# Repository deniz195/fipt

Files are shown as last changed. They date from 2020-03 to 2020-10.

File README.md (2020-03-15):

# FIPT: Fast impedance tortuosity 

FIPT is a measurement technique that allows a fast determination of the ionic resistance for battery electrodes. The technique is based on the work by J. Landesfeind ([DOI: 10.1149/issn.1945-7111](https://dx.doi.org/10.1149/2.1141607jes)) and then optimized for execution speed and reliability at [Battrion](https://battrion.com).

This repository contains the information to build an FIPT setup, prepare the electrolyte and the standard operating procedure (SOP) to successfully execute a measurement.

## Why?
The ionic resistance (or the MacMullin number) is a key performance metric for any battery electrode. It describes how easily ions can move through the electrode during fast charging or heavy use of the battery. It is therefore important for all manufacturers to optimize the ionic resistance of their electrodes.

Battrions Aligned Graphite Technology is a powerful way to reduce the ionic resistance by up to 50% through aligning graphite particles in an electrode.

## What do I need?

These are the things that you need to build your setup
- A 3D printer
- Couple of screws
- Kapton tape and 3mm foam.

Use the files in the `cad` folder and follow the assembly instructions.

Once you have the setup assembled, prepare the electrolyte. This needs:
- A salt (e.g. NaClO4)
- A solvent (e.g. EC:DMC)

The recipe for a useful electrolyte mixture is given in the `electrolyte` folder.

Finally, get your electrode, print out the SOP from the `sop` folder and get your first measurement. For this you need:
- An impendance analyzer
- Separator material
- A 200ul or 1ml pipette

In about 2-10min your measurement should be done.

## I got the data. What now?

Data analysis code is available at  [https://github.com/deniz195/fipt-analysis](https://github.com/deniz195/fipt-analysis)

## Contributing
Pull requests are welcome. For major changes, please open an issue first to discuss what you would like to change.

Please make sure to update tests as appropriate.

For questions please feel free to reach out to Deniz Bozyigit ([dbozyigit@battrion.com](mailto:dbozyigit@battrion.com))

## License
[GPL v3.0](https://choosealicense.com/licenses/gpl-3.0/)

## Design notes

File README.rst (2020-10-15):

===================================
FIPT: Fast impedance tortuosity
===================================



A fast way to get ionic resistance
==================================

.. intro-begin

FIPT is a measurement technique that allows a fast determination of the ionic resistance for battery electrodes. The technique is based on the work by J. Landesfeind (`DOI: 10.1149/issn.1945-7111 <https://dx.doi.org/10.1149/2.1141607jes>`_) and then optimized for execution speed and reliability at `Battrion <https://battrion.com>`_.

This repository contains the information to build an FIPT setup, prepare the electrolyte and the standard operating procedure (SOP) to successfully execute a measurement.

For a quick introduction `check out our video. <https://youtu.be/r1cBf72wSwA>`_ 

.. intro-end

Why?
====

.. why-begin

The ionic resistance (or the MacMullin number) is a key performance metric for any battery electrode. It describes how easily ions can move through the electrode during fast charging or heavy use of the battery. It is therefore important for all manufacturers to optimize the ionic resistance of their electrodes.

Battrions Aligned Graphite Technology is a powerful way to reduce the ionic resistance by up to 50% through aligning graphite particles in an electrode.

.. why-end

I'm sold. What do I need?
=========================

Here are the three main steps:

-	`Build your FIPT cell <https://fipt.readthedocs.io/en/latest/assembly.html>`_
-	`Get the materials <https://fipt.readthedocs.io/en/latest/materials.html>`_
-	`Measure ionic resistance (aka SOP) <https://fipt.readthedocs.io/en/latest/sop.html>`_

You find more details in the `full documentation <https://fipt.readthedocs.io/>`_

I got the data. What now?
=========================

Data analysis code is available at `fipt-analysis <https://github.com/deniz195/fipt-analysis>`_

Contribute
==========

.. contrib-begin
You can find all source files here: `<https://github.com/deniz195/fipt>`_

Pull requests are welcome. 

.. For major changes, please open an issue first to discuss what you would like to change.
.. Please make sure to update tests as appropriate.

For questions please feel free to reach out to Deniz Bozyigit (`dbozyigit@battrion.com <mailto:dbozyigit@battrion.com>`_)
.. contrib-end

License
=======
`GPL v3.0 <https://choosealicense.com/licenses/gpl-3.0/>`_

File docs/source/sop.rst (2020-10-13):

Measure ionic resistance (aka SOP)
==================================

.. include:: <isonum.txt>
.. See https://docutils.sourceforge.io/docs/ref/rst/definitions.html

.. note:: This standard operating procedure (SOP) also exists in `video form <https://www.battrion.com/fipt>`_

Prepare the workstation
-----------------------
.. warning:: When handling electrolyte always wear goggles and work in a well ventilated space.

Checklist : Gloves, googles, ethanol, wipe, FIPT cell, brush, tweezer, cutting tool, pipette, pipette tips and your electrode.

- Clean the workstation with ethanol.
- Clean the pipette, the tweezer with dry wipe.
- Set the pipette to 300ul and place the pipette tip.
- Clean all parts of the FIPT cell with the brush to remove any contamination of past measurement .
- Clean the cutting tool with the brush. Mind the blades!
- Check age of electrolyte.
- Check FIPT cell is complete: support, base, top and clamp.
- Check screw clutch setting is 0.4Nm

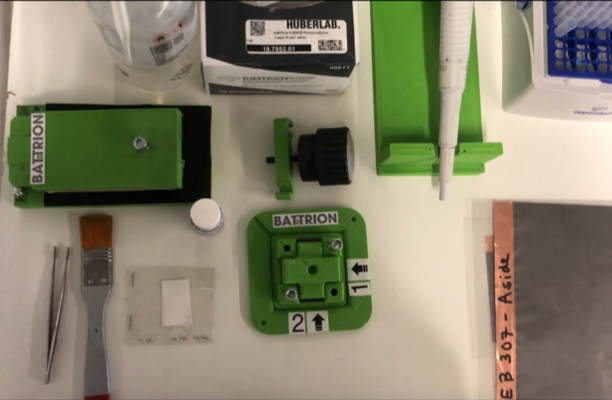
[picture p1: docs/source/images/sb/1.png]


Prepare separators
-------------------
If you have no separator pieces left, cut them in the following way:

- Cut the circular separator material (up to 3 at a time) with the triangle ruler and yellow cutting tool into **21mm wide** stripes.
- Cut the stripes into smaller pieces (21mm |times| 35mm).
- Throw out stripes with exessive wrinkling or contamination.

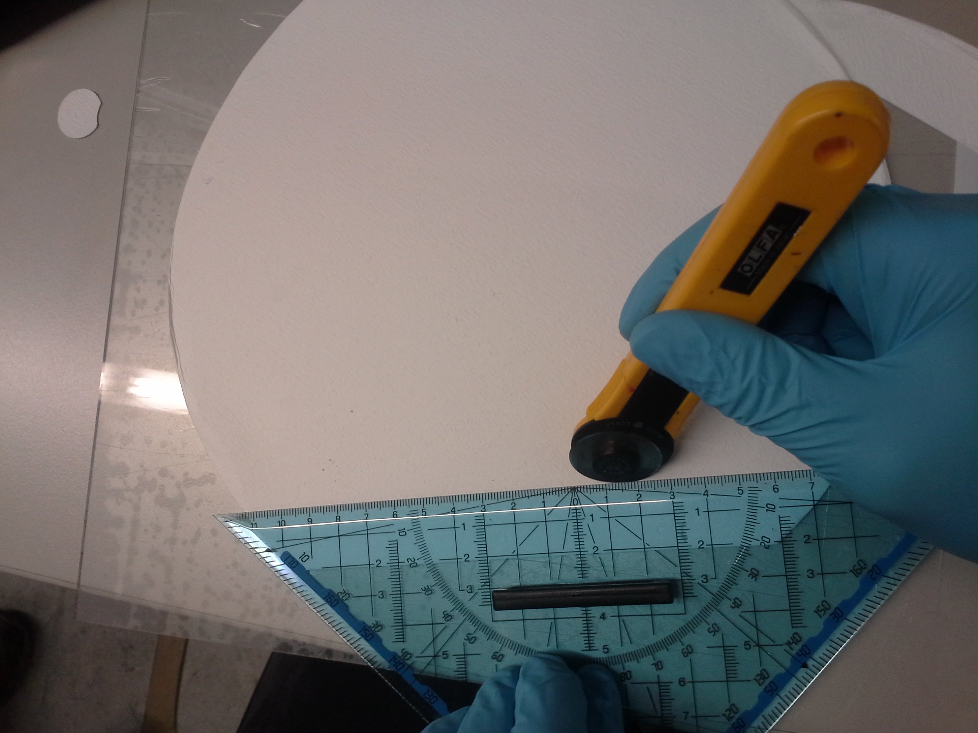
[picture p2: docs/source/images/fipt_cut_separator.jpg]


Label FIPT cell
---------------
- Clean the label on the cell wih ethanol.
- Write the new label of the electrode and precise the side that you want to measure.

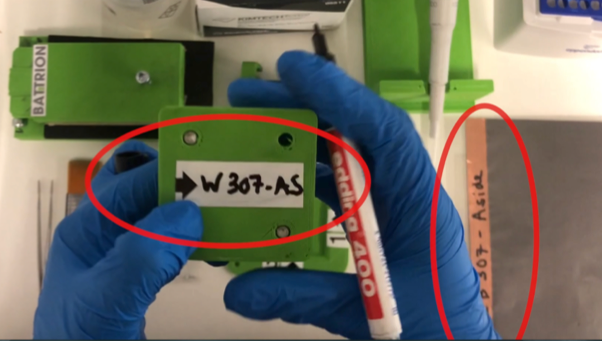
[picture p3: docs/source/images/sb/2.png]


Cut the electrode
-----------------
Checklist : Cutting tool, tweezer and your electrode labeled.

- Place the electrode on the cutting tool.
- Press the blades down to cut out the electrode strip.
- Collect the electrode strip with the tweezer.
- Check the edges of the strip are clean after cutting. The electrode strip should be **20mm wide**.
- Repeat the cutting for two strips total.

.. note:: Keep track of which side of the electrode you want to measure!

..  image:: images/sb/3.png
    :width: 45%

Assemble the FIPT cell
----------------------
Checklist : FIPT cell, tweezer, pipette, separator, electrolyte and 2 strips of electrode.

.. warning:: All orientation markers of the FIPT cell should point to top-left.

- Place the first strip orthogonal to the foam of the FIPT cell. Face up the side that you want to measure. 
- Place one separator on the middle of the electrode strip in the FIPT cell gap. 
- Check that separators sits stable in the center.

..  image:: images/sb/4.png
    :width: 45%

- Apply 300ul of electrolyte to the center of the separator.

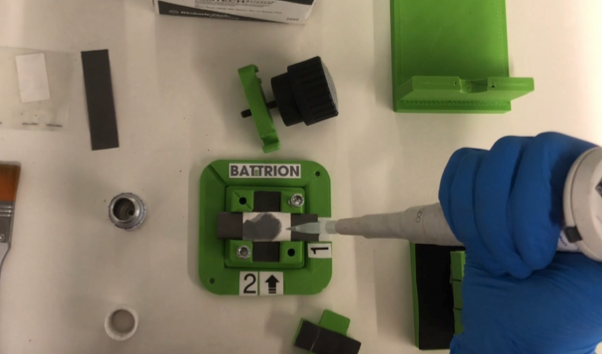
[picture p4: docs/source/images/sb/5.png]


- Place the second strip on the top of the separator, orthogonal to the first strip. Face down the side that you want to measure.

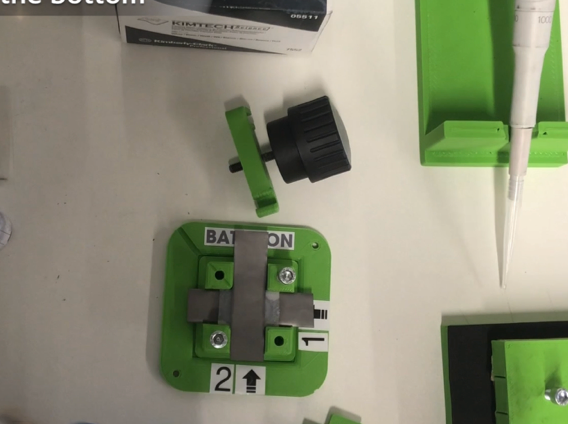
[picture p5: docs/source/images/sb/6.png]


- Close the cell by adding the top.
- Check that the orientation markers are aligned.
    
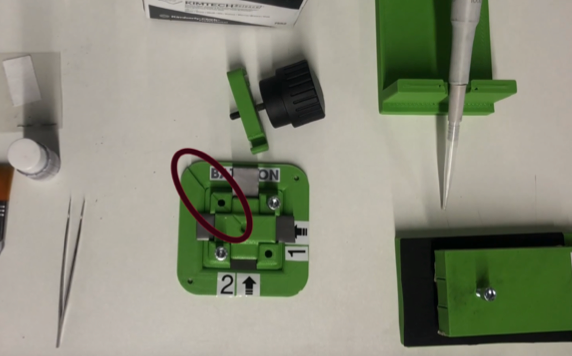
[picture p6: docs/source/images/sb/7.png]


- Mount the top clamp.
- Screw in the middle screw until the clutch of screw triggers (you will hear a click sound).

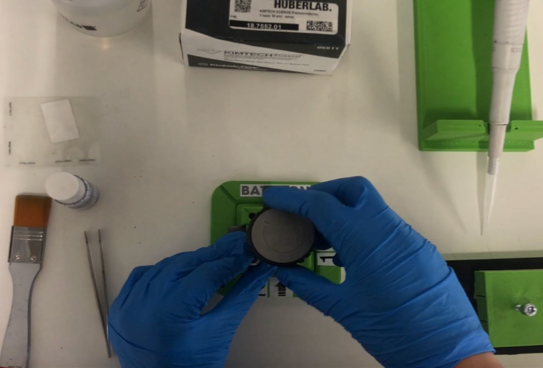
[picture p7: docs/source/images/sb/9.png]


Run the measurement
-------------------

- Attach 2 measurement wires to the strips of the electrode to connect the FIPT cell to an impedance analyzer.

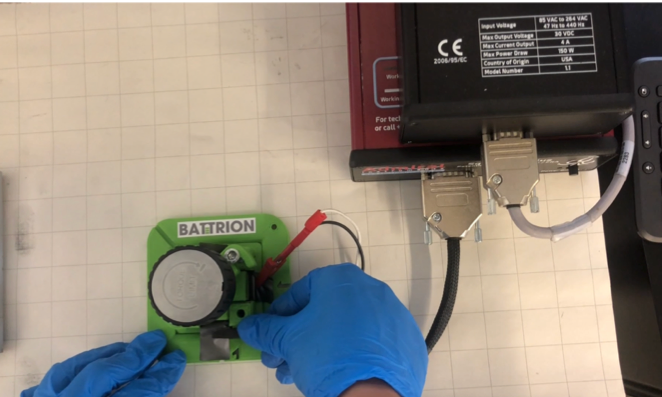
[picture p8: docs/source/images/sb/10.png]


- Set up the measurement.

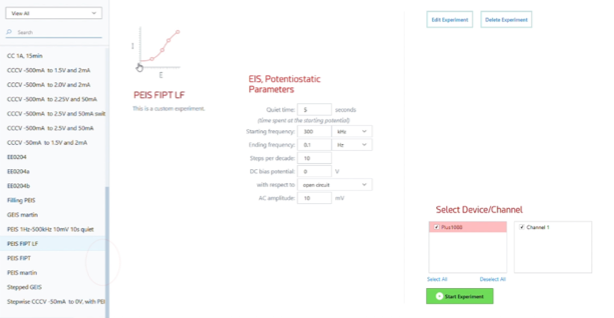
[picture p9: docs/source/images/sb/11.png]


- Carry out the FIPT measurement and determine the ionic resistance of your electrode.
- Note that a good graph looks like a hockey stick.

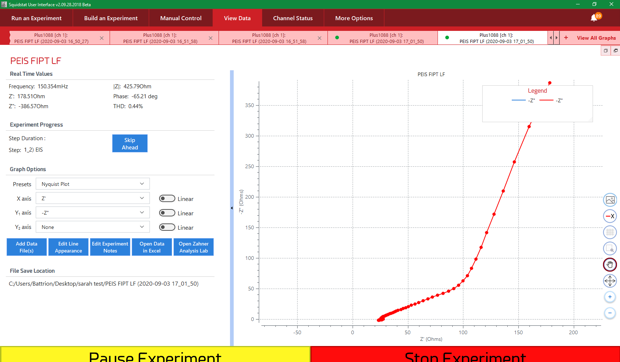
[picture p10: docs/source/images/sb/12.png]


.. note:: To achieve reliable data, do a total of 3 measurements per sample

Analyze your data
-----------------

A typical data set looks like this:

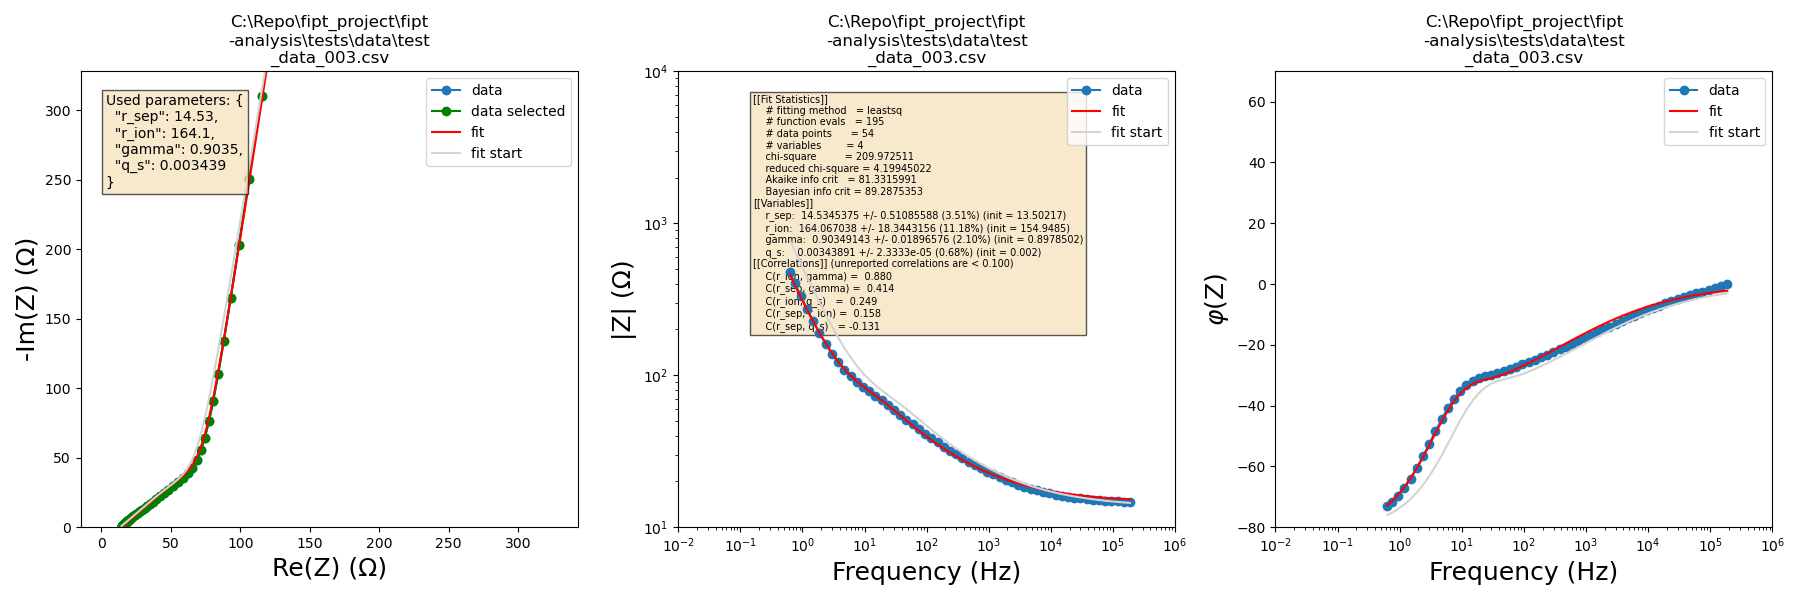
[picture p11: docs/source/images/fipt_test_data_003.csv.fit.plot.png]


To see how to analyze your FIPT data using our `fipt-analysis <https://github.com/deniz195/fipt-analysis>`_ , watch our follow up `video on our website <https://www.battrion.com/fipt>`_

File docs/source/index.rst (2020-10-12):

.. fipt documentation master file, created by
   sphinx-quickstart on Thu May 14 15:04:23 2020.
   You can adapt this file completely to your liking, but it should at least
   contain the root `toctree` directive.

===================================
FIPT: Fast impedance tortuosity
===================================

A fast way to get ionic resistance
==================================

.. include:: ../../README.rst
   :start-after: intro-begin
   :end-before: intro-end

Why?
====

.. include:: ../../README.rst
   :start-after: why-begin
   :end-before: why-end

I'm sold. What do I need?
=========================

If you want to get started quickly, you can order the complete `FIPT kit on our website <https://www.battrion.com/fipt/>`_. Otherwise you can build it yourself. Here are the three main steps:

.. toctree::
   :maxdepth: 1

   assembly
   materials
   sop

I got the data. What now?
=========================

Data analysis code is available at `fipt-analysis <https://github.com/deniz195/fipt-analysis>`_

Contribute
============

.. include:: ../../README.rst
   :start-after: contrib-begin
   :end-before: contrib-end

Indices and tables
==================

* :ref:`genindex`
* :ref:`search`

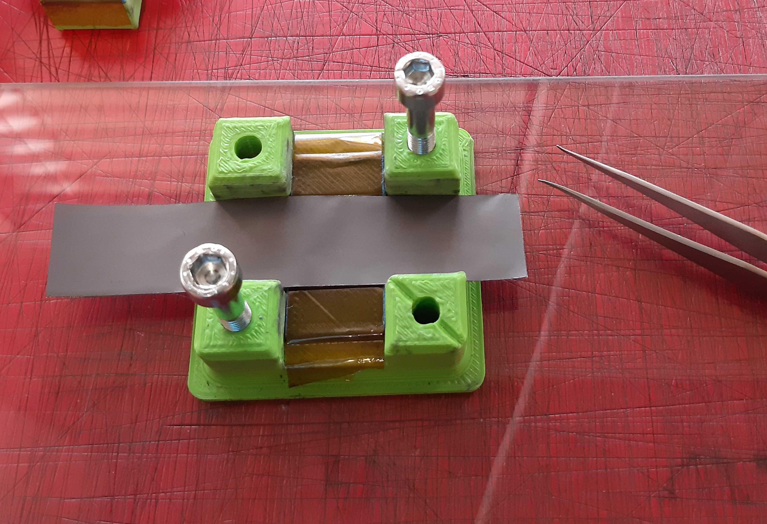
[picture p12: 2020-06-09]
docs/source/images/fipt_put_1stripe.jpg

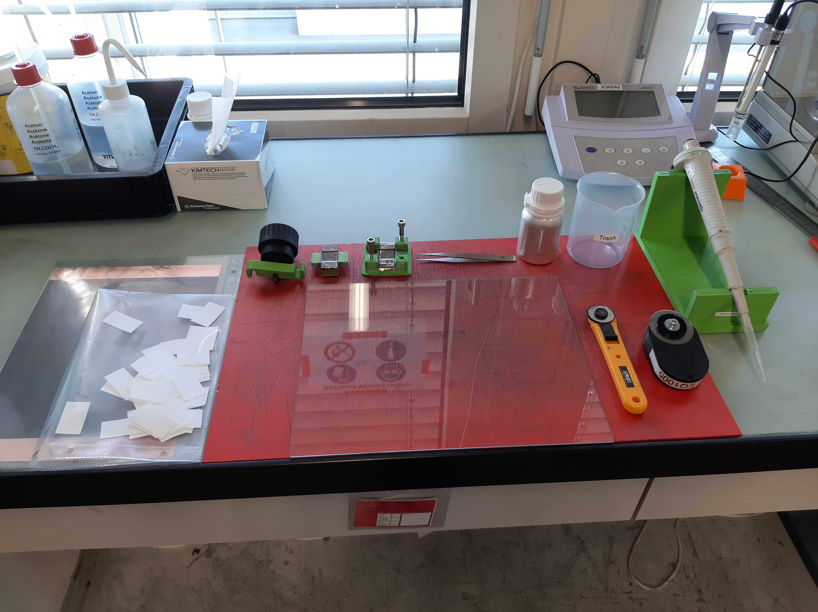
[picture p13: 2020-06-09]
docs/source/images/fipt_workstation_01.jpg

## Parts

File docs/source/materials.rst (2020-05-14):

Get the materials
=================

.. include:: <isonum.txt>
.. See https://docutils.sourceforge.io/docs/ref/rst/definitions.html

You will need these materials to make a successful FIPT measurement:

-   Your electrode (2 |times| 20mm |times| 50mm per measurement)
-   Separator material 
-   Non-intercalating electrolyte

Separator material
------------------

While many different separators can be used, this one works well:

GE Healthcare Whatman |trade|, 1820-240, 250um glass fiber

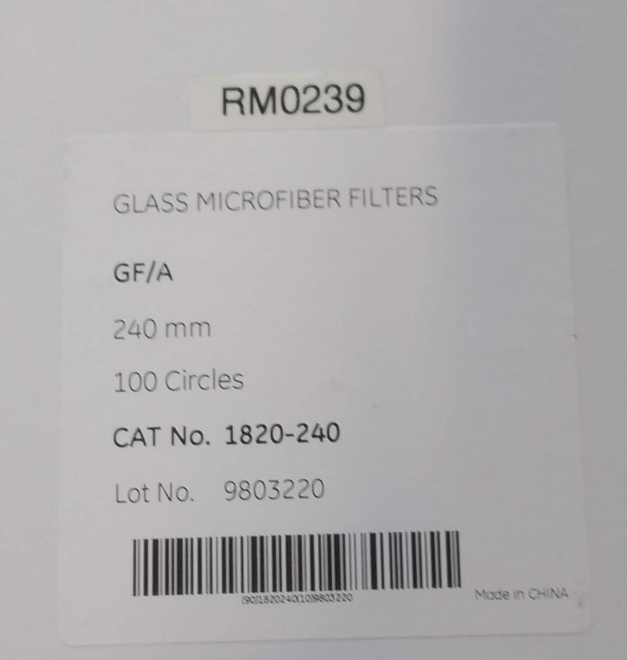
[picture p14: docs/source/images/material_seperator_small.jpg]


Electrolyte
-----------

For the FIPT measurement a weakly conducting, non-intercalating electrolyte is used. We typically use the following electrolyte (ID: RM296):

:Description: 0.020 mol/kg NaClO4 in EC:DMC 3:7 (w/w)
:Condictivity at 25degC:  0.658 mS / cm (temperature coefficient: 1.31% / ΔdegC)

If you want to make it yourself, you need two materials: 

:Salt: Sodium perchlorate monohydrate (SigmaAldrich 310514-100G,
  CAS Number 7791-07-3)

:Solvent: EC:DMC 3:7 (w/w)

Then you mix them:

-   use 100ml vial
-   add 60g of EC:DMC 3:7 (w/w)
-   add 168.5mg Salt (RM0292, CAS Number 7791-07-3)
-   mix well

If the electrolyte is well closed (parafilm), it can used in ambient conditions for up to 4 weeks. Note that a shift in conductivity can happen (+10%) over time, which should be accounted for by regular measurement of the conductivity.

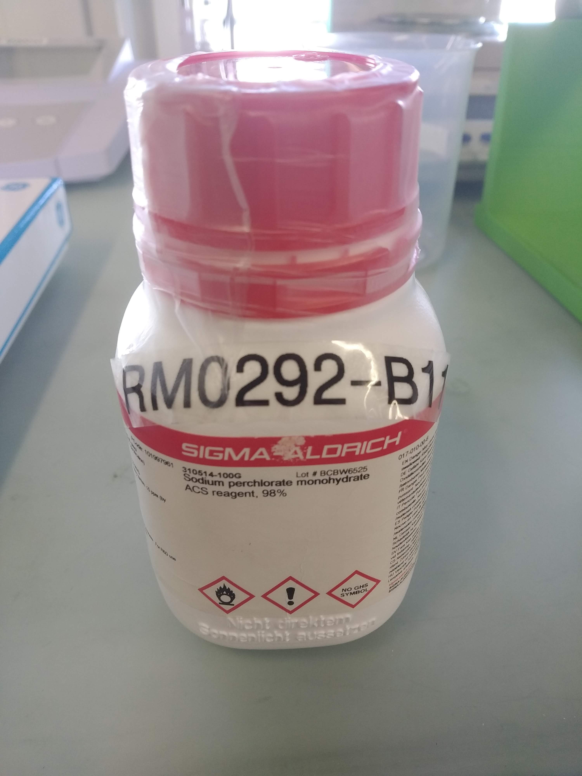
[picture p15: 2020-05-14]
docs/source/images/material_salt.jpg

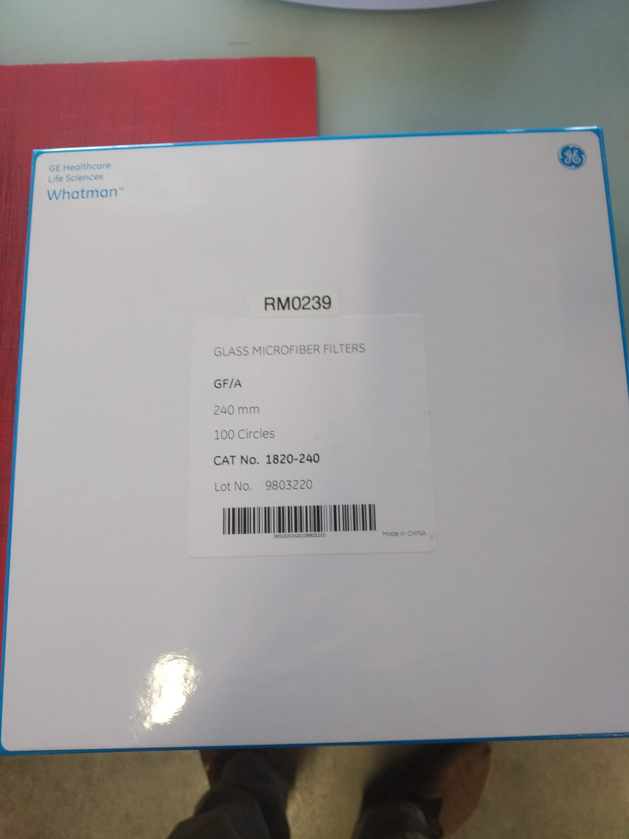
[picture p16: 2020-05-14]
docs/source/images/material_seperator.jpg

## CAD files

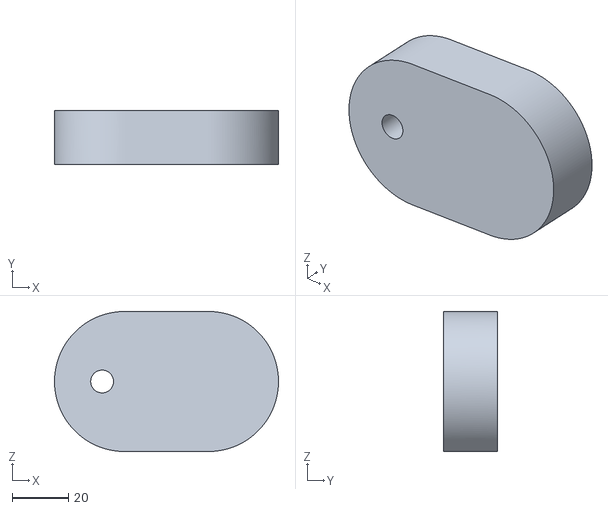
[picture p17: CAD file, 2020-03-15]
cad/cutter/071_0205_RollCutter20mmCenter8mm.stl
80.0 x 19.2 x 50.0

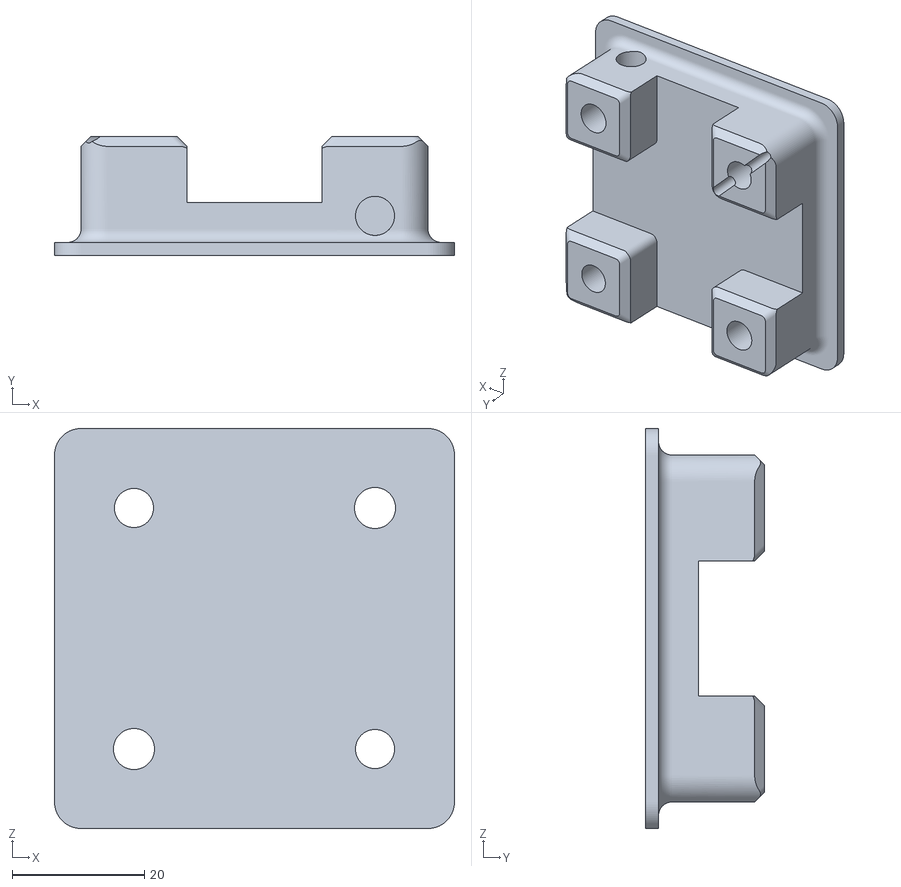
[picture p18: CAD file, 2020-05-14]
cad/fipt_cell/071_0100_Base.stl
60.4 x 18.0 x 60.4

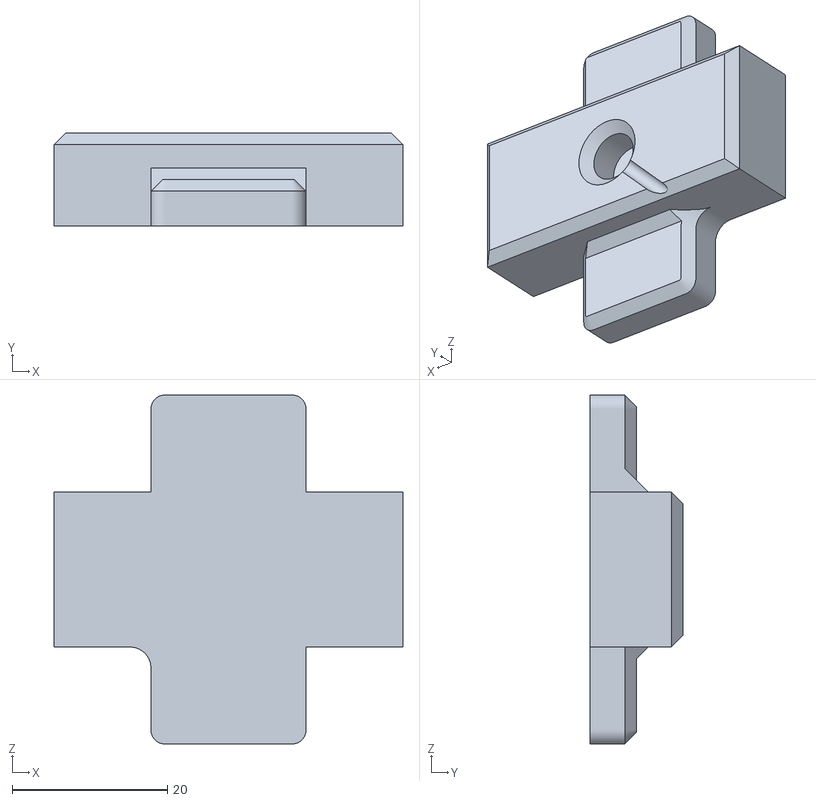
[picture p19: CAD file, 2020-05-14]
cad/fipt_cell/071_0101_Top.stl
45.0 x 12.0 x 45.0

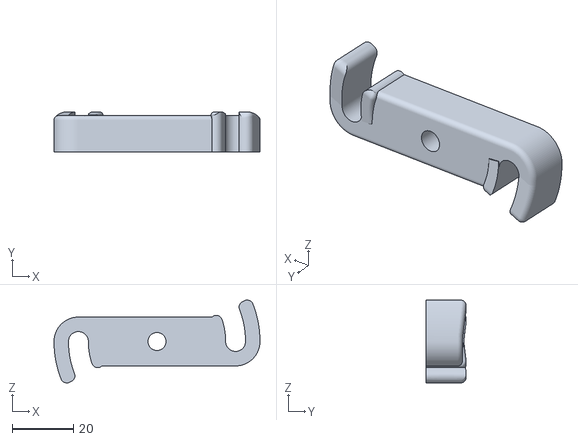
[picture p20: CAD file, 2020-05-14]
cad/fipt_cell/071_0102_Clamp.stl
67.5 x 13.2 x 27.1

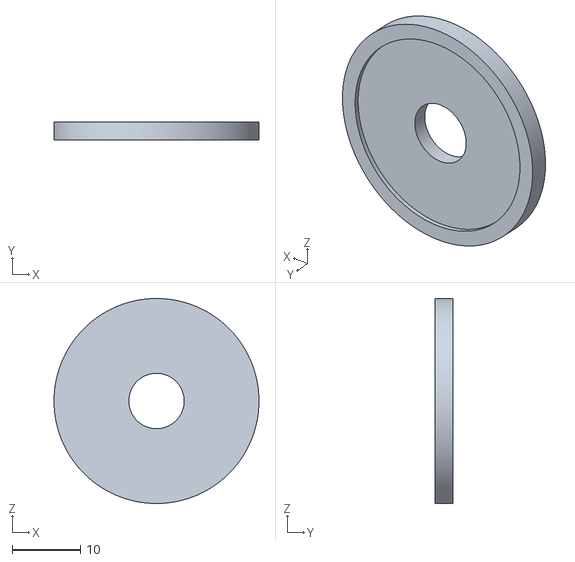
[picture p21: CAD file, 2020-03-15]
cad/cutter/071_0204_RollCutter20mmScrewClamp8mm.stl
30.0 x 2.60 x 30.0

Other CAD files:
cad/cutter/071_0204_RollCutter20mmScrewClamp8mm.ipt
cad/cutter/071_0205_RollCutter20mmCenter8mm.ipt
cad/fipt_cell/071_0100_Base.ipt
cad/fipt_cell/071_0101_Top.ipt
cad/fipt_cell/071_0102_Clamp.ipt
cad/fipt_cell/071_0105_ScrewCap.ipt
cad/fipt_cell/071_0121_FoamKapton_short.ipt
cad/fipt_cell/071_0122_FoamKapton_long.ipt
cad/fipt_cell/071_1000_fipt_cell.iam
cad/fipt_cell/components/ISO 4762 - M5 x 40ISO.ipt
cad/fipt_cell/components/ISO 4762 - M6 x 40ISO.ipt
cad/fipt_cell/components/Torque limiting knob screw GN 5910-47-M6-30-1-SW.ipt

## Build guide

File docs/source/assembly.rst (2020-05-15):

Build your FIPT cell
=====================

Get necessary items
-------------------

3D-printed parts:

-	``base``: `071_0100_Base.stl <https://github.com/deniz195/fipt/blob/master/cad/fipt_cell/071_0100_Base.stl>`_
-	``top``: `071_0101_Top.stl  <https://github.com/deniz195/fipt/blob/master/cad/fipt_cell/071_0101_Top.stl>`_
- 	``clamp``: `071_0102_Clamp.stl <https://github.com/deniz195/fipt/blob/master/cad/fipt_cell/071_0102_Clamp.stl>`_

Print settings: Typically PLA, 250um layer height, 500um nozzle diameter. Note that the models need 90deg turn for printing

Other parts:

-   3x M5x40mm hex socket bolts
-   20mm wide Kapton tape
-   >= 20mm wide double sided tape
-   2-3mm thick EVA foam rubber sheet (from arts and crafts store)

Assemble
--------

1.  Add foam to ``base`` and ``top`` in the pictures below. The foam parts consists of 3 layers: 

    -   Double sided tape
    -   Foam sheet
    -   Kapton tape 

2.  Make sure they are 20mm wide and that Kapton covers all foam (such that no electrolyte is absorbed).
3.  Screw two M5 into the ``base`` until they are flush at the bottom
4.  Screw one M5 through the middle of the ``clamp``

This is how the final result should look like:

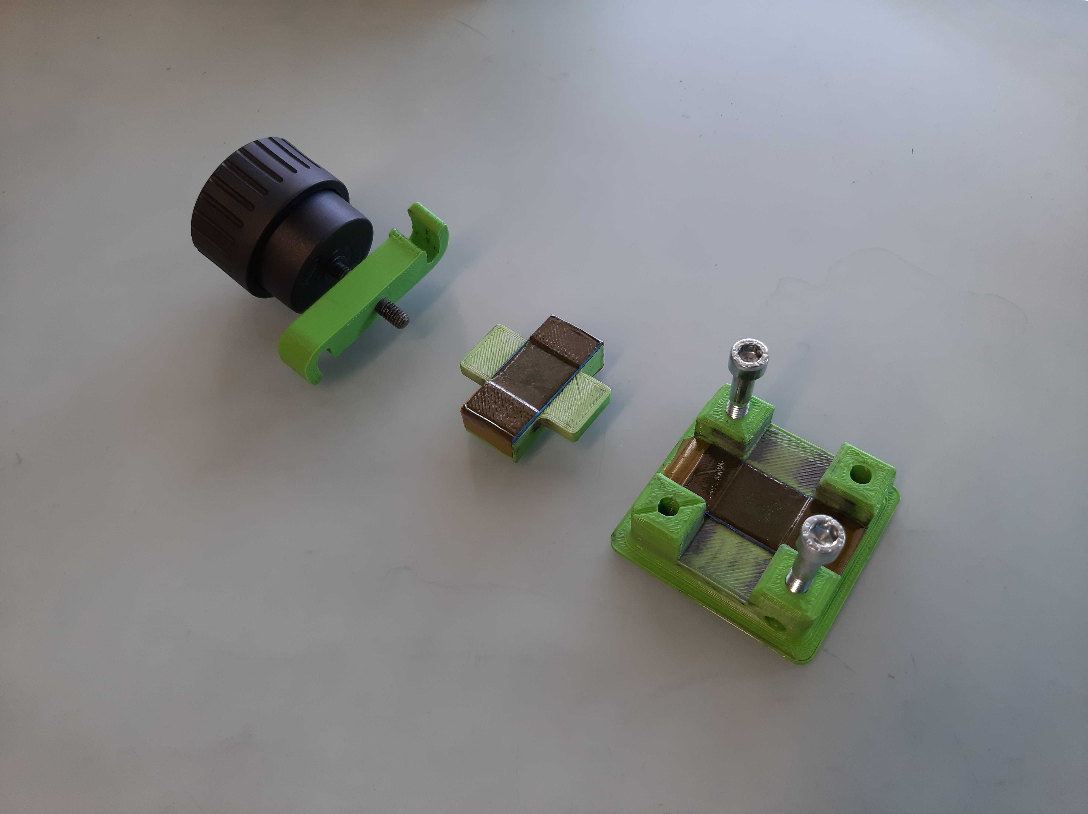
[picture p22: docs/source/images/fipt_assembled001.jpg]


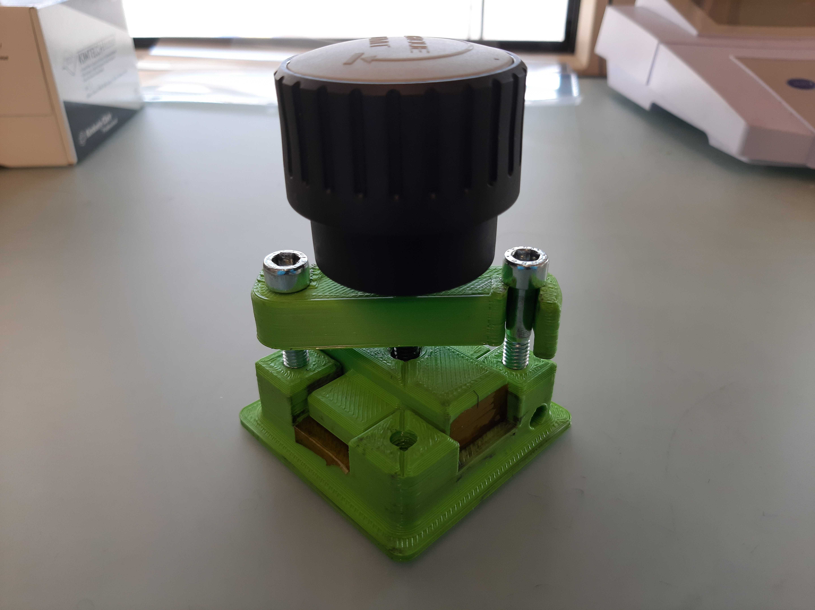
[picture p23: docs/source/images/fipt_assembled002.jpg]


.. warning:: The foam parts are necessary to avoid touching of the edges of the crossing electrodes. Please follow the order/orientation of the SOP exactly. Otherwise, shorting and other problems can regularly occur!

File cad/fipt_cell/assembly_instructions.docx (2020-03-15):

Assembly instructions FIPT cell

# Revision table

Date | Person | Rev# | Comment
191205 | DB | 001 | First version

Note: create new file for each revision. Increment revision number in file name

Note: save a new file/revision before starting to change stuff

# Summary

Necessary items:

- 3x M5x40mm hex socket bolts
- 3d printed parts: (Typically: PLA, 250um layer height, 500um nozzle diameter)
  - 071_0100_Base.stl
  - 071_0101_Top.stl
  - 071_0102_Clamp.stl
  - 071_0105_ScrewCap.stl
- 20mm wide Kapton tape
- >= 20mm wide double sided tape
- 2-3mm thick EVA foam rubber sheet (from arts and crafts store)

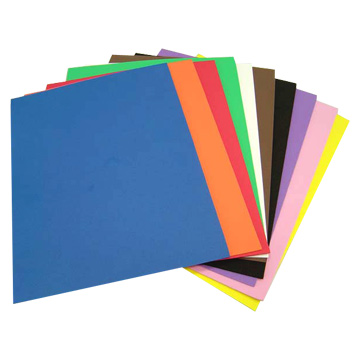
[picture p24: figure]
Plain EVA Rubber Sheet

Assembly steps:

1) Print all items
2) Add foam to Top part and Base part as in pictures below.

These foam parts consists of 3 layers:

  a. Double sided tape
  b. Foam sheet
  c. Kapton tape

Make sure they are 20mm wide and that Kapton covers all foam (such that no electrolyte is absorbed).

Note: The foam parts are necessary to avoid touching of the edges of the crossing electrodes. Please follow the order/orientation of the SOP exactly. Otherwise, shorting and other problems can regularly occur!

# Assembly pictures

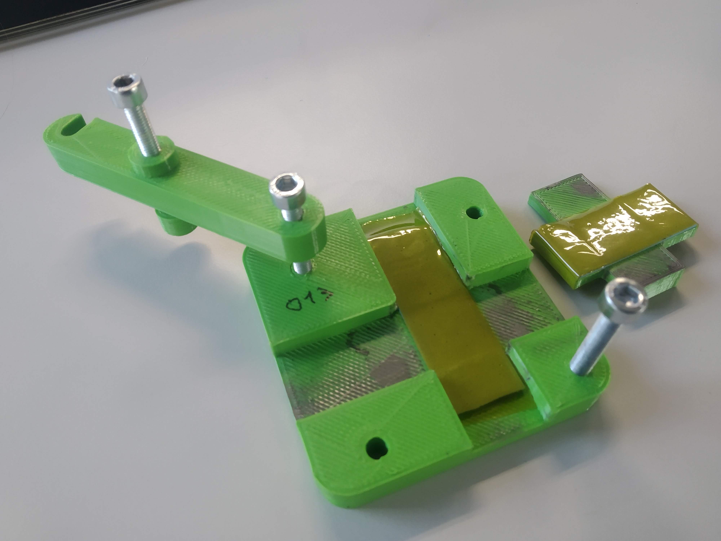
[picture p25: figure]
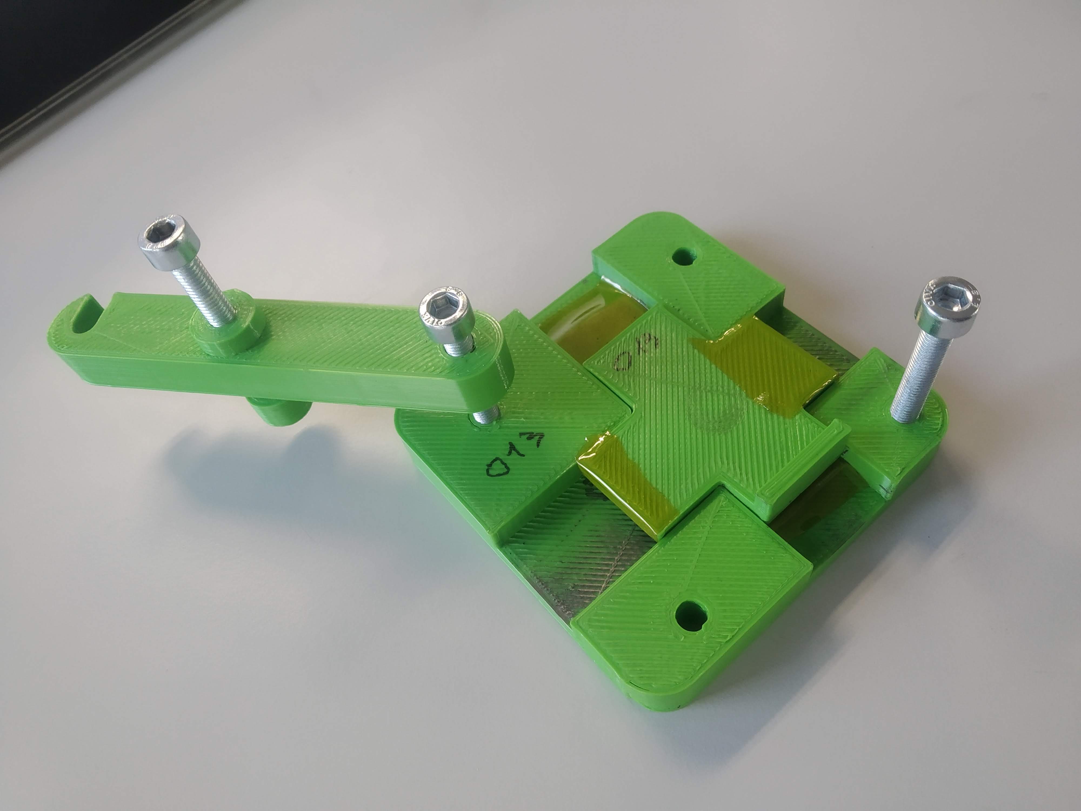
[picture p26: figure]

[Type text][Type text][Type text]

assembly_instructions.docx © BATTRION AG 20183 / 3 CONFIDENTIAL

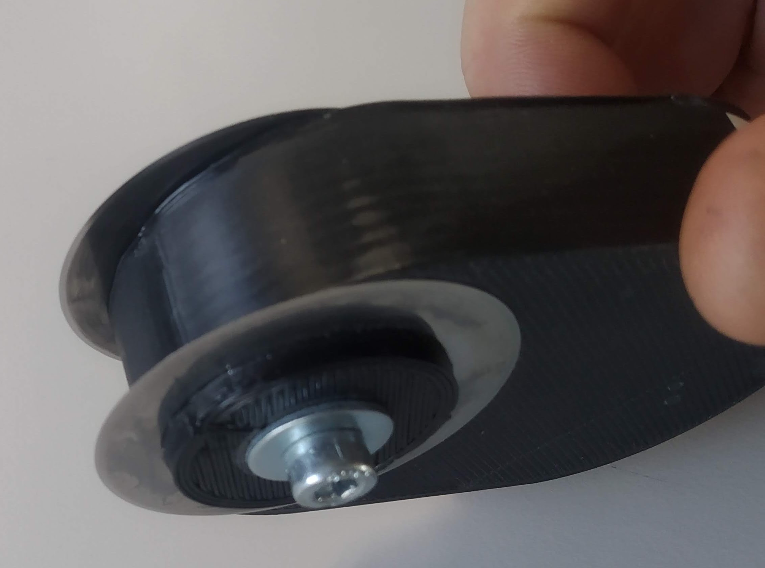
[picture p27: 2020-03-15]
cad/cutter/cutter_assembled001.jpg

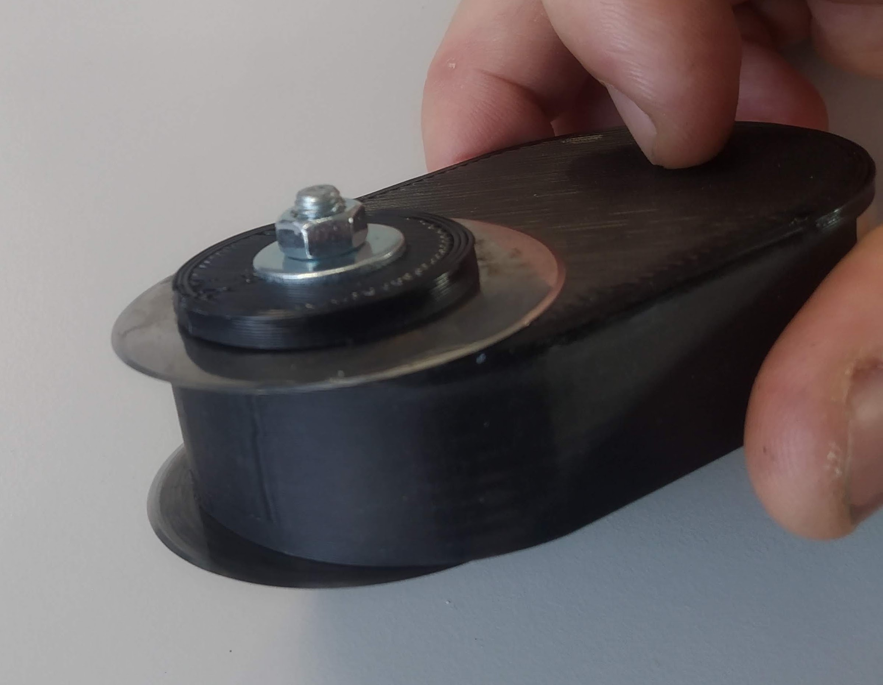
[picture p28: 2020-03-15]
cad/cutter/cutter_assembled002.jpg

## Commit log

2020-04-29 added full fipt cell assembly. added gitignore.
    [071_0100_Base.ipt, 071_0101_Top.ipt, 071_0102_Clamp.ipt, 071_0105_ScrewCap.ipt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]
2020-04-29 first version of torque limiting knob screw design.
    [071_0100_Base.ipt, 071_0101_Top.ipt, 071_0102_Clamp.ipt, 071_1000_fipt_cell.iam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]
2020-04-29 improved dimensions for fast printing and usability
    [071_0100_Base.ipt, 071_0101_Top.ipt, 071_0102_Clamp.ipt, 071_0122_FoamKapton_long.ipt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]
2020-04-29 updated stl files
    [071_0100_Base.stl, 071_0101_Top.stl, 071_0102_Clamp.stl, 071_0105_ScrewCap.stl]
2020-05-05 improved usability.
    [071_0100_Base.ipt, 071_0100_Base.stl, 071_0101_Top.ipt, 071_0101_Top.stl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]
2020-05-14 improved design for usability and torque screw
    [071_0100_Base.ipt, 071_0100_Base.stl, 071_0101_Top.ipt, 071_0101_Top.stl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]
2020-05-14 added sop and assembly
